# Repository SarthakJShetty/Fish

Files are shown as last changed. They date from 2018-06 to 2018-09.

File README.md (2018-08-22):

# Open Source Robotic Fish

This repository is dedicated to the development of the predatory robotic fish, developed at the [Theoretical Ecology and Evolution Laboratory](https://teelabiisc.wordpress.com/ "TEE-Lab, IISc"), [Indian Institute of Science](https://www.iisc.ac.in "Indian Institute of Science, Bengaluru").

### :warning: Code is buggy :warning:

### Introduction:
The robotic fish developed was used to study the aggregation and swarming characteristics of the <em><a title="Serpae tetra" href="https://en.wikipedia.org/wiki/Serpae_tetra" target="_blank">Serpae tetra</a></em> species of fish.

### Construction:
 - The body of the Fish is made of extruded polystyrene (thermocol). The [design](https://github.com/SarthakJShetty/Fish/tree/master/Design_Files/Mechanical_Design/Structure_Design "Mechanical Designs") was made in SolidWorks, and carved using a crafting blade.

 - The Fish is maneuvered using a joystick controller through the [pygame](Pygame.org "pygame") library for Python. A list of supported controllers is given [here](https://www.pygame.org/docs/ref/joystick.html "pygame"). We have tried out a number of joysticks, such as the [XBox 360 controller](https://www.amazon.com/Xbox-360-Wireless-Controller-Packaging-Black/dp/B073WJCQGT/ref=sr_1_4?ie=UTF8&qid=1530160595&sr=8-4&keywords=xbox+360+controller "XBox 360 controller"), and the [Logitech Extreme 3D Pro Gamepad](https://www.amazon.com/Extreme-3D-Pro-Joystick-Windows/dp/B00009OY9U/ref=sr_1_1?s=videogames&ie=UTF8&qid=1530160648&sr=1-1&keywords=logitech+extreme+pro "Logitech Extreme 3D Pro").

 - The Fish is controlled through an Arduino UNO, which communicates with the computer running ```pygame``` through a [Bluetooth module](https://www.amazon.com/HiLetgo%C2%AE-Wireless-Bluetooth-Transceiver-Arduino/dp/B071YJG8DR/ref=sr_1_1_sspa?ie=UTF8&qid=1530698951&sr=8-1-spons&keywords=hc05&psc=1 "HC-05 Bluetooth Module"), mounted on it's head.

 - A [SHARP Distance Sensor GP2Y0A21YK0F](https://www.pololu.com/category/79/sharp-distance-sensors "Sharp Distance Sensor GP2Y0A21YK0F") was used to judge the distance between the fish and obstacles up ahead.

 - The Fish was encased in a layer of polythene to ensure waterproofing while operating underwater. Specifically, the joints between successive links was encased in a skin-like layer of polythene.

 - The necessary propelling movements were provided by a series of 3 [Tower SG90 Servo Motors](https://servodatabase.com/servo/towerpro/sg90 "Tower S690 Servo Motors").

 - A pair of [9V batteries](https://www.amazon.com/AmazonBasics-Everyday-Alkaline-Batteries-8-Pack/dp/B00MH4QM1S "9V Batteries") were used in series to provide the necessary electric power for the operation of the fish.

### Fritzing Diagram:
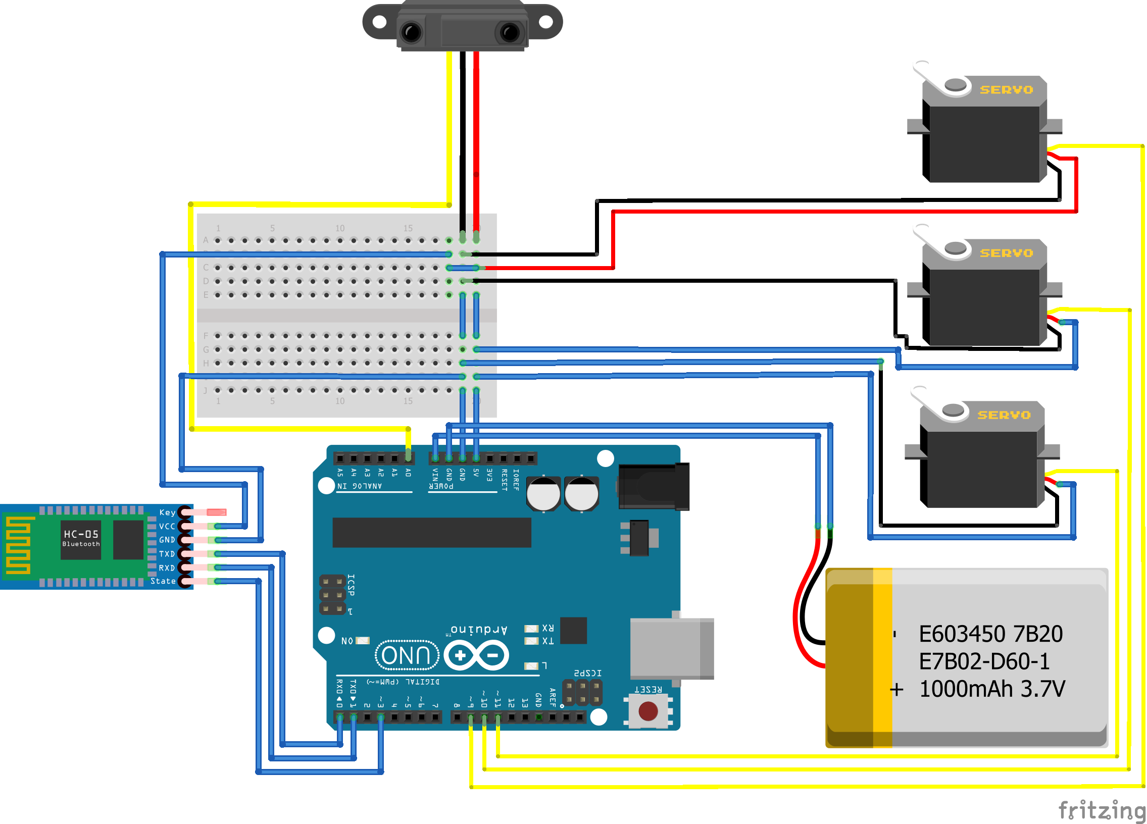
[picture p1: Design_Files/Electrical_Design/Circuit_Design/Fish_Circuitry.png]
Fritzing Diagram

<figcaption align="center"><strong>Fig 1.</strong><em> Fritzing diagram of electrical wiring.</em>
<em><strong>Note:</strong> 3.7V LiPo is for representation purposes only.</em></figcaption>

### SolidWorks Model:
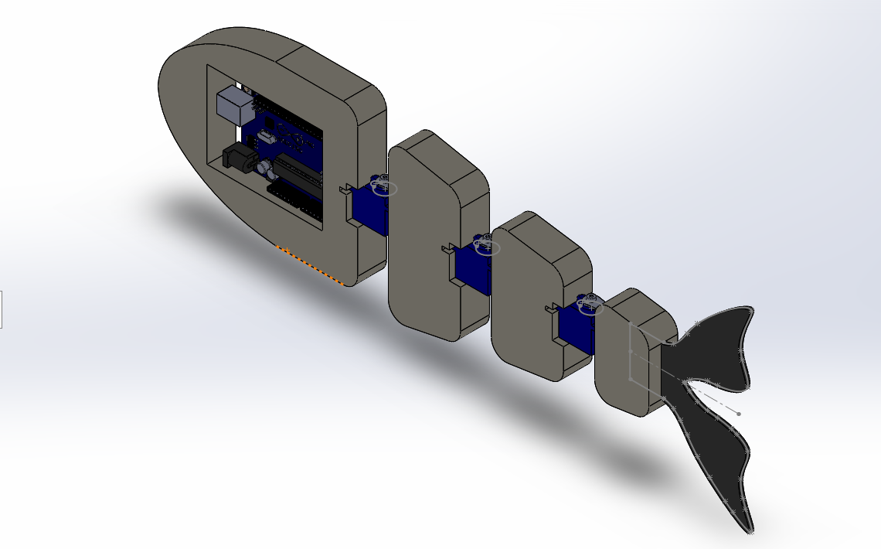
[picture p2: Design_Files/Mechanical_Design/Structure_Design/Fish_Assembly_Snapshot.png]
SolidWorks Model

<figcaption align="center"><strong>Fig 2.</strong><em> SolidWorks assembly of mechanical structure.</em></figcaption>

### Command Flowchart:
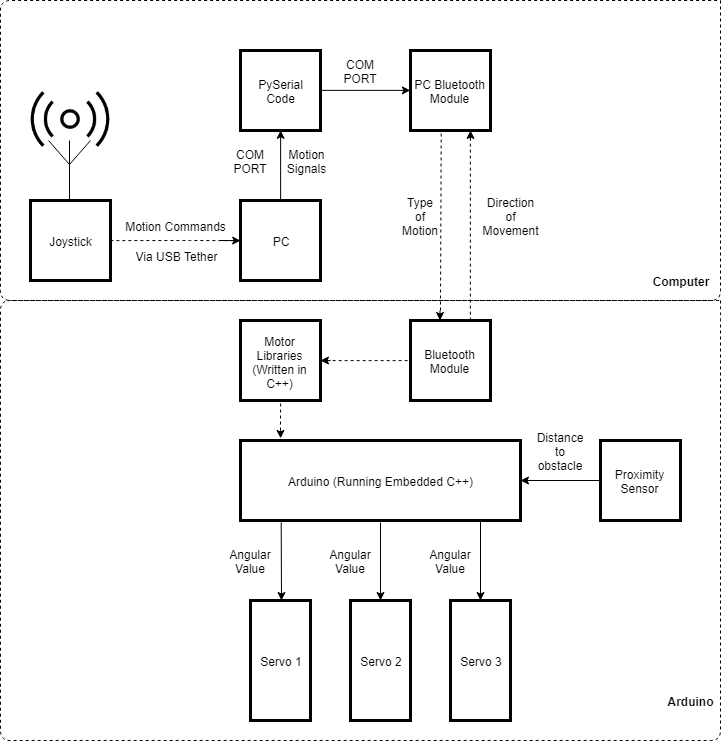
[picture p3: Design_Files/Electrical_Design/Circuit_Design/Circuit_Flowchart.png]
Command flowchart

<figcaption align="center"><strong>Fig 3.</strong><em> Flowchart of commands.</em></figcaption>

### Working:
 1. The electrical connections are made as shown in the <a title="Fritzing Diagram" href="https://github.com/SarthakJShetty/Fish/master/Design_Files/Electrical_Design/Circuit_Design/Fish_Circuitry.png" alt="Fritzing Diagram">Fritzing diagram</a>.

 2. Once the connections are made and checked (to prevent short circuiting underwater!), the batteries are connected to the battery headers provided in the circuit.

 3. The SHARP sensors are obstructed to check if the necessary commands are executed (in this case the ```C_MOVE()``` function would be executed).

 4. Once the [Joystick.py](https://github.com/SarthakJShetty/fish/tree/master/Code/Joystick_Code/Joystick_Code.py) has been executed, wait for 5 seconds as the [EEPROM_Code.cpp](https://github.com/SarthakJShetty/Fish/tree/master/Code/CPP_Code/EEPROM_Flush_Code.cpp) script executes and flushes the EEPROM on-board the UNO to prevent interferences from previous stored values.

 5. The Fish can be maneuvered as required using the left analog stick of the joystick. Three movements are possible:
	- [Forward](https://github.com/SarthakJShetty/Fish/tree/master/Code/CPP_Code/Stable_Movement_Code.cpp)- The Fish moves in an S-type movement.
	- [Left](https://github.com/SarthakJShetty/Fish/tree/master/Code/CPP_Code/Stable_Movement_Code.cpp)- The Fish moves in a C-type movement, deflecting towards the left.
	- [Right](https://github.com/SarthakJShetty/Fish/tree/master/Code/CPP_Code/Stable_Movement_Code.cpp)- The Fish moves in a C-type movement, deflecting towards the right.
	- [Obstacle Avoidance](https://github.com/SarthakJShetty/Fish/tree/master/Code/CPP_Code/Stable_Movement_Code.cpp)- The Fish moves in a C-type movement, deflecting towards the left. 

 6. The Fish operates either through the controls of the user, through the joystick, or it continuously moves in an S-type fashion, until it encounters an obstacle, thereafter which it executes a C-type movement.

### Build-log:
You can check out the <a title="Build-log" href="https://github.com/SarthakJShetty/Fish/tree/master/build-log.md">build-log</a> for a detailed progress report.

### Known Issues:

 1. Occasionally, the Bluetooth module on-board losses communication link with the Bluetooth on the PC. When this happens, close the pygame dialog and rerun the Joystick_Code.py script to establish control once again (<strong>this issue has now been resolved by connecting the Bluetooth module to a 3.3V voltage supply.</strong>)

 2. The Arduino will reboot, if sufficient power is not provided. Thus, we suggest the use of LiPo batteries to provide a more reliable and lasting power source. We are currently using <a title="12V LiPo battery" href="" target="_blank">12V, 2000mAh LiPo batteries</a> (testing this right now).

 3. Communication link between the UNO and the computer will not be active until the `EEPROM_Flush_Code.cpp` has been executed (approx 5 seconds), thereafter which the LED on the UNO associated with GPIO pin 13 will glow a bright orange (depending on the make of the Arduino board).

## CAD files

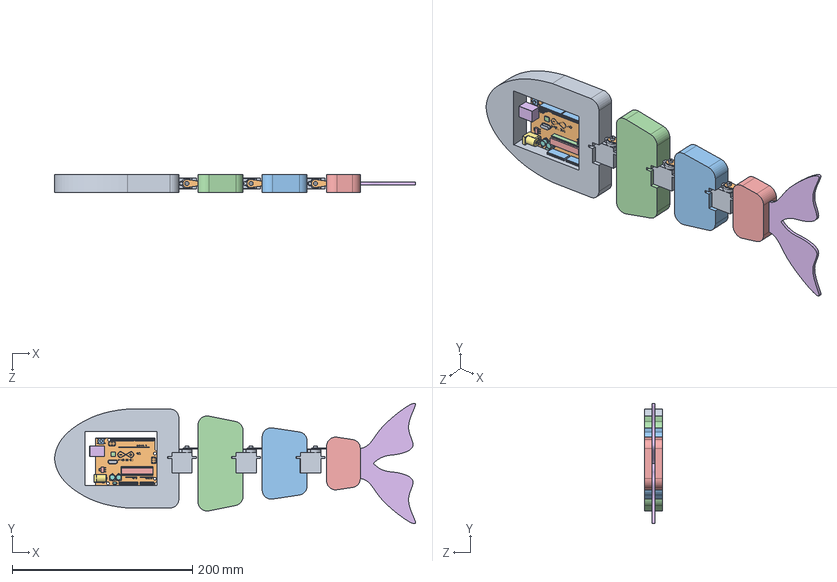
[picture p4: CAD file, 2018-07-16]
Design_Files/Mechanical_Design/Structure_Design/Fish_Assembly.SLDASM
401.1 x 133.8 x 20.0 mm
PCB UNO
Buton
base chip
foot (chip) x 4
foot (big chip) x 24
Condensateur x 2
Crystal
ICSP x 2
Pins Connection Shield
Small Chip
Transistor
USB
Alimentation
Resistance
Servo Motor (SG90) x 3
Servo_Horn x 3
Tail_Fin

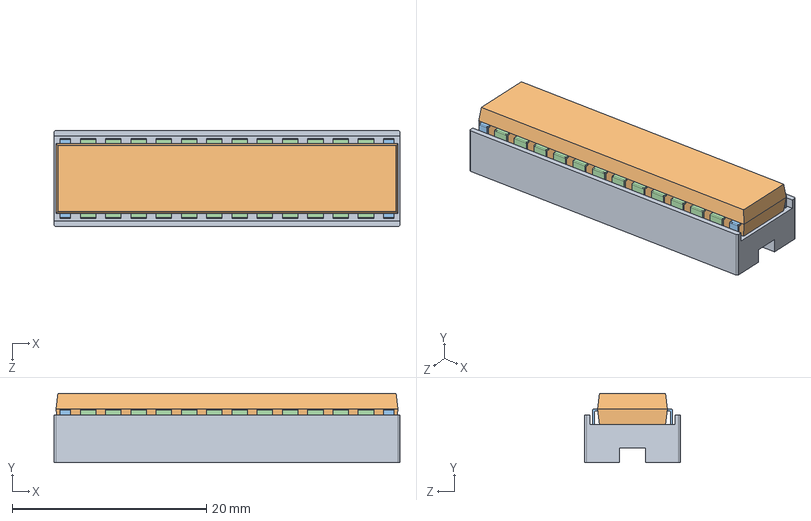
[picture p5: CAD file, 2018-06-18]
Design_Files/Electrical_Design/Arduino_Design/Chip.SLDASM
35.6 x 7.10 x 9.90 mm
base chip
foot (chip) x 4
foot (big chip) x 24

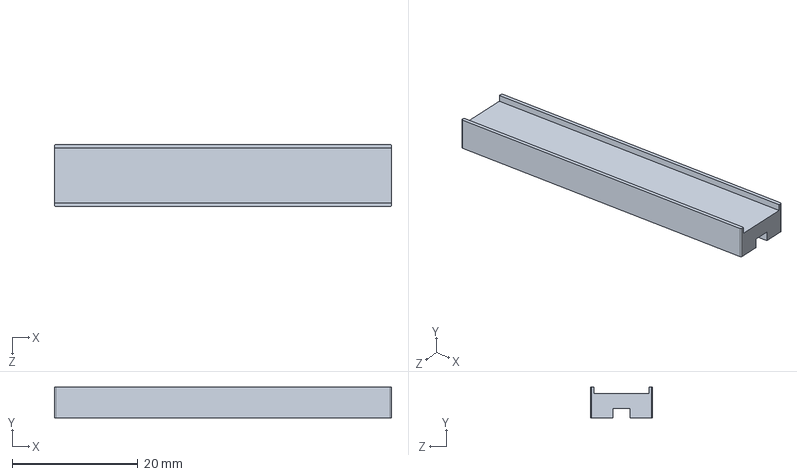
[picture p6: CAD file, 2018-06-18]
Design_Files/Electrical_Design/Arduino_Design/base chip.SLDPRT
53.6 x 4.90 x 9.90 mm

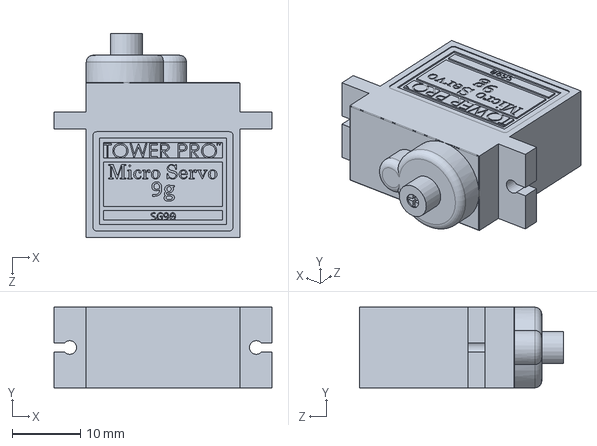
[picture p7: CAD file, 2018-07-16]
Design_Files/Mechanical_Design/Servo_Design/Servo Motor (SG90).SLDPRT
31.9 x 11.8 x 29.9 mm

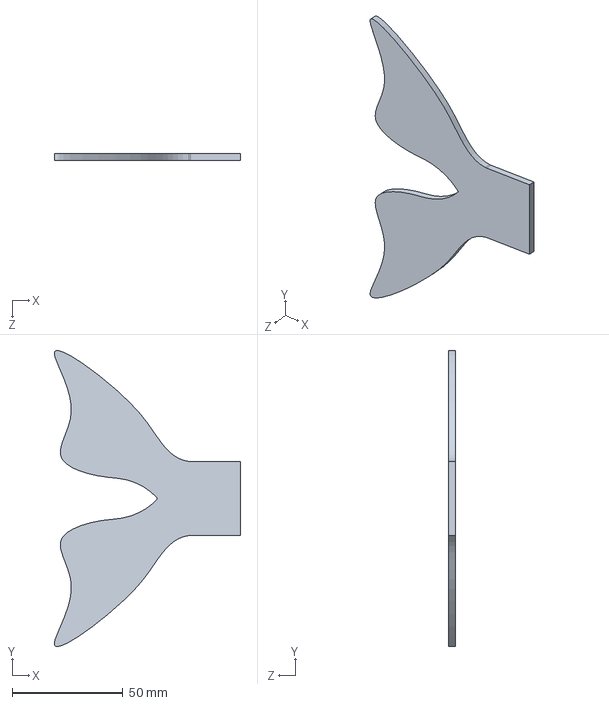
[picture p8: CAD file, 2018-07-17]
Design_Files/Mechanical_Design/Structure_Design/Tail_Fin.SLDPRT
84.3 x 133.8 x 3.00 mm

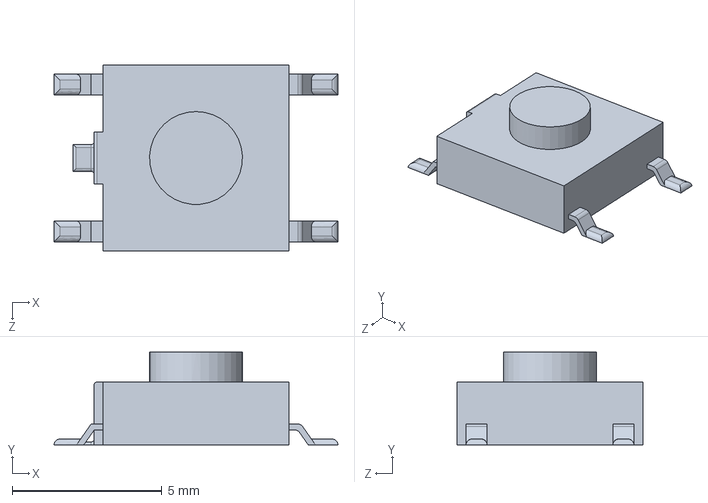
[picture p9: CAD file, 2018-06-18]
Design_Files/Electrical_Design/Arduino_Design/Buton.SLDPRT
9.48 x 3.10 x 6.20 mm

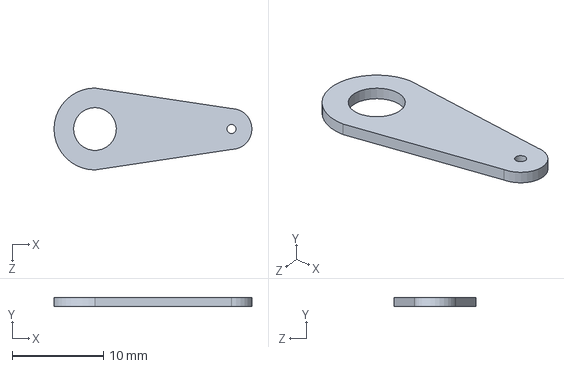
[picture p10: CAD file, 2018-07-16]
Design_Files/Mechanical_Design/Servo_Design/Servo_Horn.SLDPRT
21.8 x 1.00 x 9.00 mm

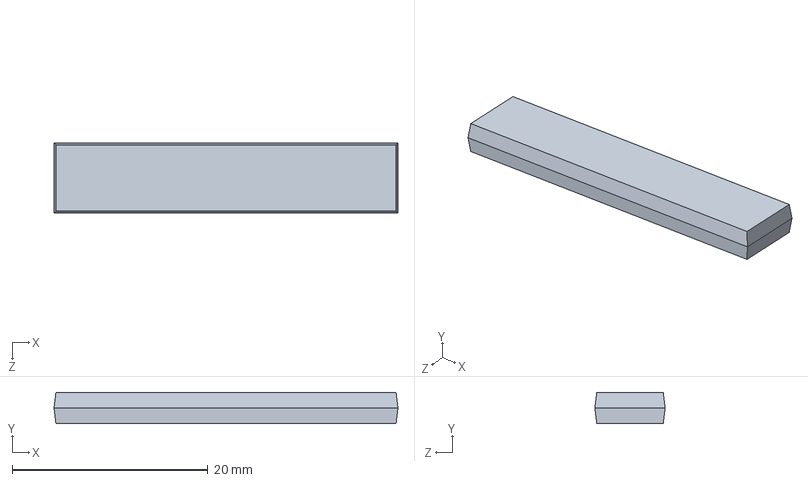
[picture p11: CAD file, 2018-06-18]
Design_Files/Electrical_Design/Arduino_Design/box.SLDPRT
35.2 x 3.20 x 7.19 mm

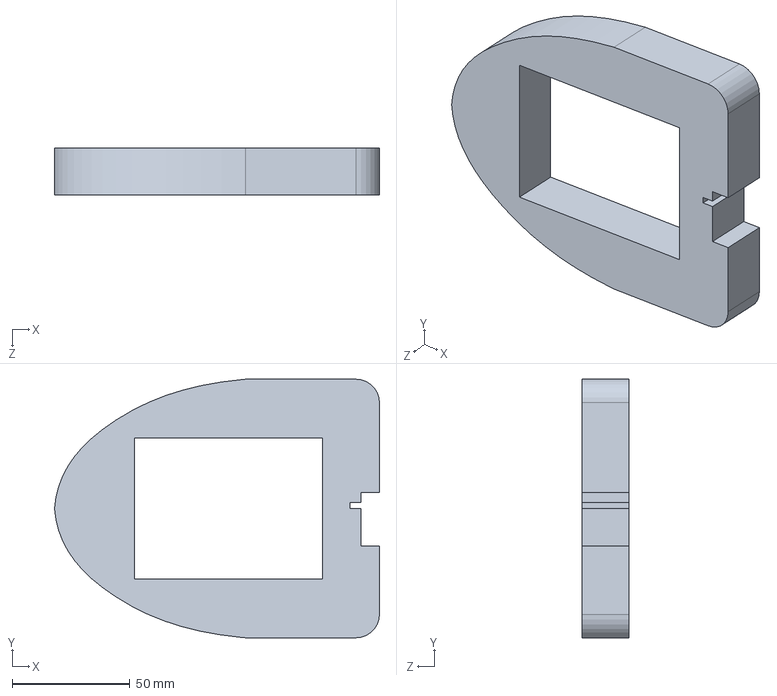
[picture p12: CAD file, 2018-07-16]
Design_Files/Mechanical_Design/Structure_Design/Body.SLDPRT
138.2 x 110.0 x 20.0 mm

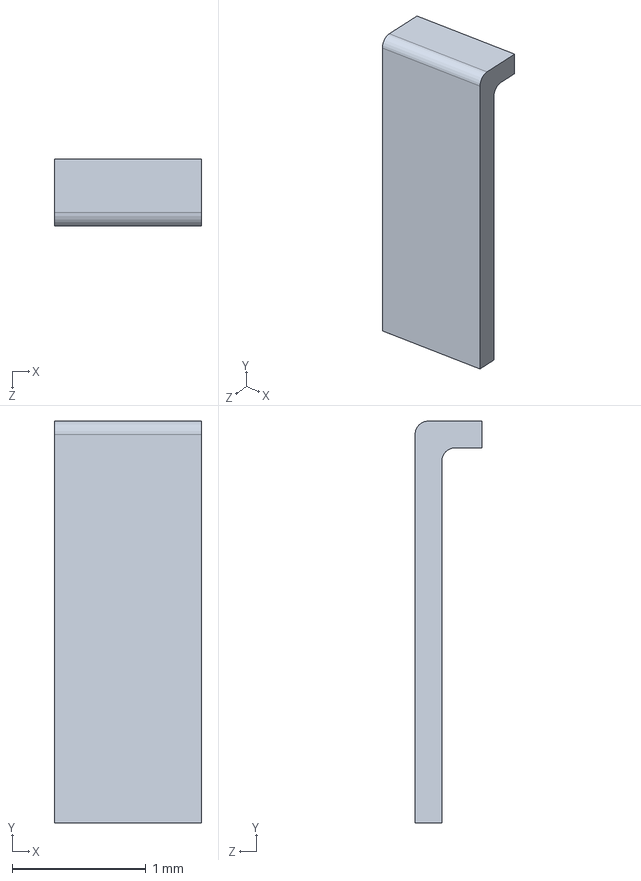
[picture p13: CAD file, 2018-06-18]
Design_Files/Electrical_Design/Arduino_Design/foot (chip).SLDPRT
1.10 x 3.00 x 0.5 mm

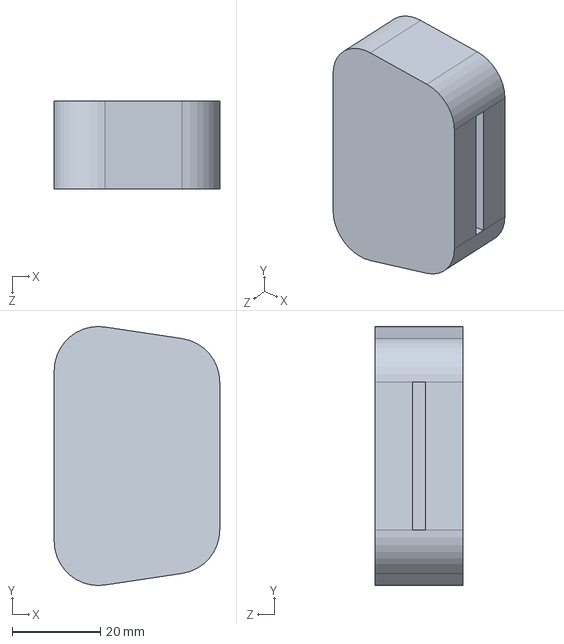
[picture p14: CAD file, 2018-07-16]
Design_Files/Mechanical_Design/Structure_Design/Body_4.SLDPRT
37.5 x 58.6 x 20.0 mm

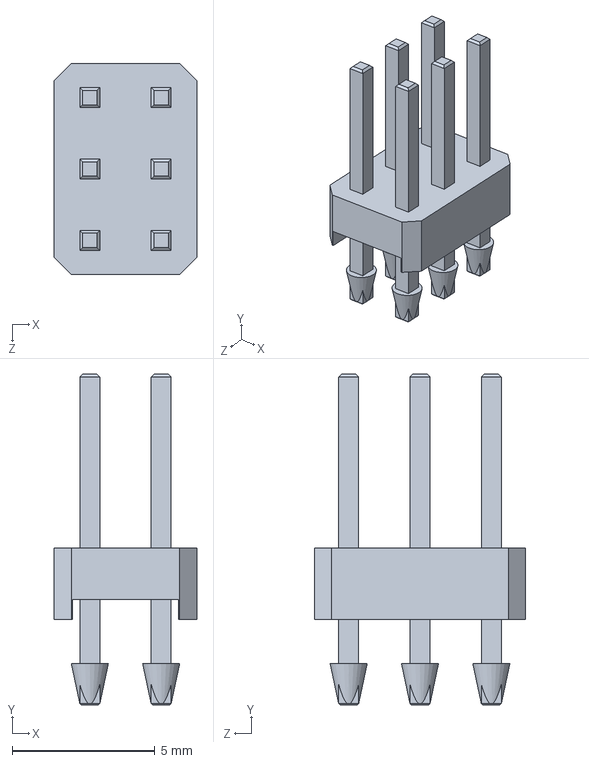
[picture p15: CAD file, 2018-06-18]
Design_Files/Electrical_Design/Arduino_Design/ICSP.SLDPRT
5.00 x 11.6 x 7.40 mm

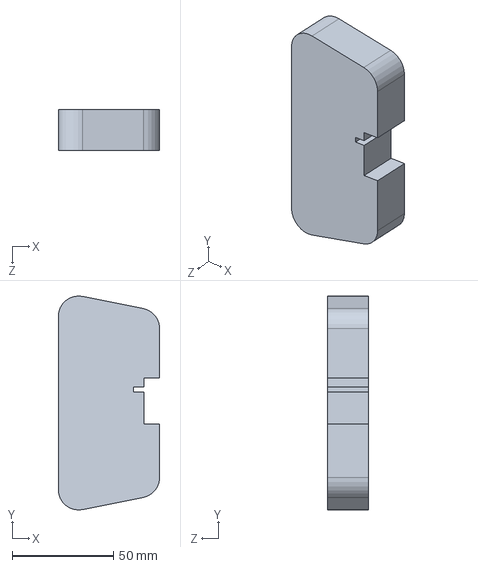
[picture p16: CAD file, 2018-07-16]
Design_Files/Mechanical_Design/Structure_Design/Body_2.SLDPRT
50.0 x 105.6 x 20.0 mm

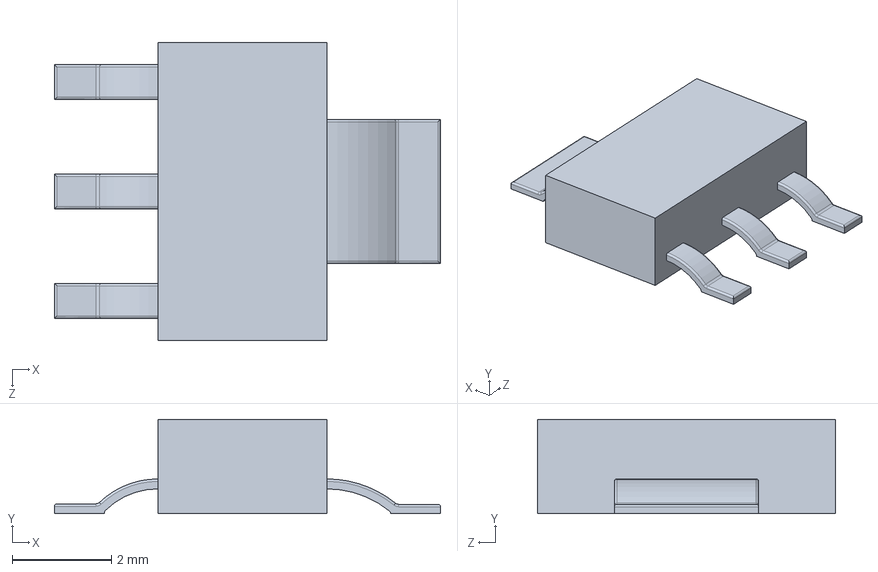
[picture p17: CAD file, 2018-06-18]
Design_Files/Electrical_Design/Arduino_Design/Transistor.SLDPRT
7.76 x 1.90 x 6.00 mm

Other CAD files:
Design_Files/Mechanical_Design/Structure_Design/Body_3.SLDPRT
Design_Files/Electrical_Design/Arduino_Design/foot (big chip).SLDPRT
Design_Files/Electrical_Design/Arduino_Design/Alimentation.SLDPRT
Design_Files/Electrical_Design/Arduino_Design/Condensateur.SLDPRT
Design_Files/Electrical_Design/Arduino_Design/Crystal.SLDPRT
Design_Files/Electrical_Design/Arduino_Design/PCB UNO.SLDPRT
Design_Files/Electrical_Design/Arduino_Design/Pins Connection Shield.SLDPRT
Design_Files/Electrical_Design/Arduino_Design/Resistance.SLDPRT
Design_Files/Electrical_Design/Arduino_Design/USB.SLDPRT
Design_Files/Mechanical_Design/Structure_Design/Fish_Assembly.SLDDRW

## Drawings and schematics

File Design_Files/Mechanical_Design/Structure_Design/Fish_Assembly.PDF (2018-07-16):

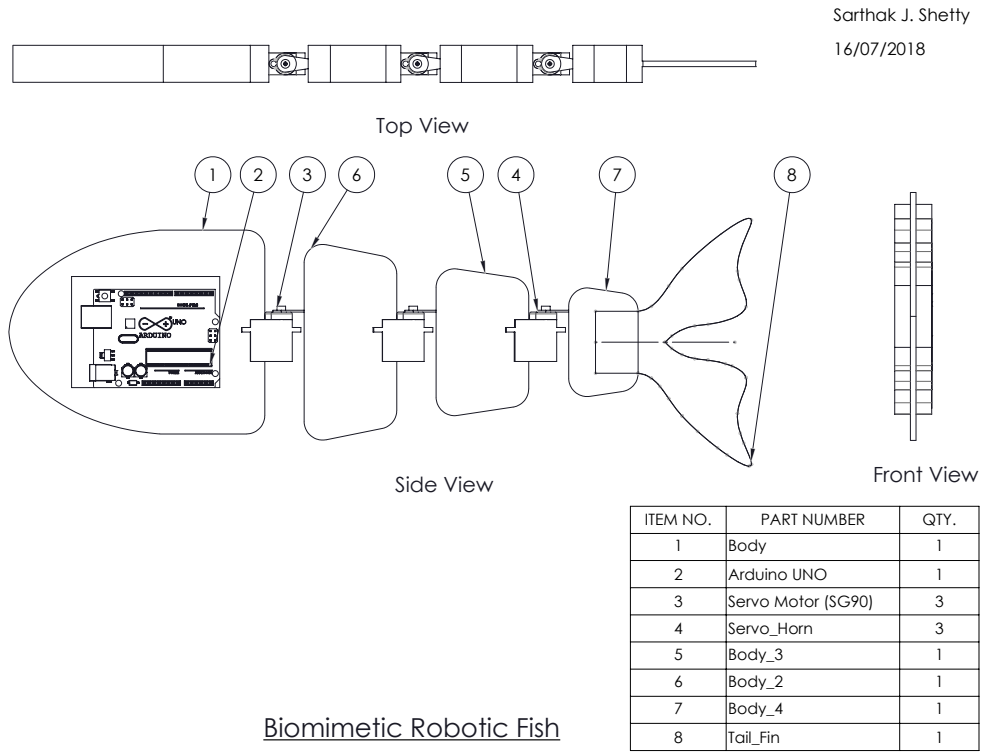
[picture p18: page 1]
Sarthak J. Shetty; Side View; Top View; Front View

ITEM NO. | PART NUMBER | QTY.
1 | Body | 1
2 | Arduino UNO | 1
3 | Servo Motor (SG90) | 3
4 | Servo_Horn | 3
5 | Body_3 | 1
6 | Body_2 | 1
7 | Body_4 | 1
8 | Tail_Fin | 1

Biomimetic Robotic Fish

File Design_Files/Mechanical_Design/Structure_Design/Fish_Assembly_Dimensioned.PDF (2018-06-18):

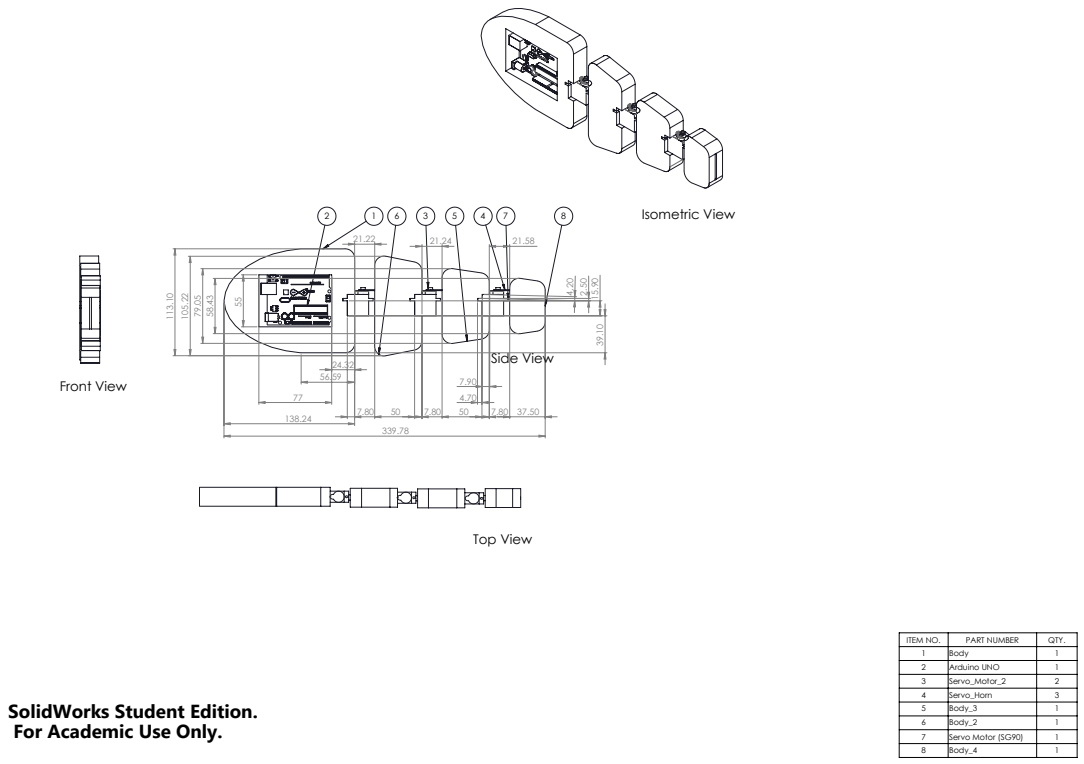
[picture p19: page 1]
Side View; Isometric View; Front View; Top View

ITEM NO. | PART NUMBER | QTY.
1 | Body | 1
2 | Arduino UNO | 1
3 | Servo_Motor_2 | 2
4 | Servo_Horn | 3
5 | Body_3 | 1
6 | Body_2 | 1
7 | Servo Motor (SG90) | 1
8 | Body_4 | 1

SolidWorks Student Edition.
For Academic Use Only.

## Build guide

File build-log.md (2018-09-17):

### Progress Log:

- <strong>Date:</strong> 28/05/2018
	- Just wrote code.
	- Yet to implement on Arduino.
 	- Will be doing that tomorrow.
 	- Need to add a <a title="README.md" target="_blank" href="https://github.com/SarthakJShetty/Fish/blob/master/README.md">README</a>.

- <strong>Date:</strong> 29/05/2018
 	- Code now works with sensor.
 	- Added a piece of code to convert volts to distance.

- <strong>Date:</strong> 60/05/2018
 	- Updated Bluetooth Code.
 	- Bluetooth now works over COM4 port.
 	- ```println()``` statements look much cleaner now

- <strong>Date:</strong> 31/05/2018
 	- Added EEPROM flush. Not much of an improvement.
 	- Bluetooth has not been integrated here.
	- Bluetooth code has been introduced, albeit very buggy as of now.

- <strong>Date:</strong> 08/05/2018
 	- Joystick can be used to control the fish now. Attempting on a wired controller though.
 	- Interference. Need to upload a SLAVE communication.

- <strong>Date:</strong> 09/06/2018
 	- DualShock3 replaced with XBox 360 Wireless knockoff controller.
 	- Works much better now.
 	- SLAVE protocol has been established. Works much better.

- <strong>Date:</strong> 10/06/2018
 	- BLuetooth module has been converted into a one-way system, i.e. slave communication
 	- RX/TX can be connected simultaneously, no obstruction to communication from controller.

- <strong>Date:</strong> 13/06/2018
 	- Code has been successfully tested on fish.
 	- This code has been converted into a ```.cpp``` library, to make the Arduino code cleaner.

- <strong>Date:</strong> 15/06/2018
 	- The thermocol has ripped. Adhesive applied and trying to fix it.
 	- Code seems to be working well. Angles seem to be too big though.

- <strong>Date:</strong> 03/07/2018
	- Embargo due to mechanical issues.
	- A polythene wrapper has been used as a final layer for waterproofing the structure.
	- The issue is with fit. Almost fixed it.
	- Should have a great Fish by this weekend. Fingers crossed.
	- Try to code a more harmonic motion of Fish body.

- <strong>Date:</strong> 09/07/2018
	- Movement seems to work well, even without harmonic motion integration.
	- <strong>Important:</strong>```ICSP``` pins should not be used for power supply. ```V(in)``` pin solely supports 5V. ```V(in)``` should be used, along with corresponding ```GND``` pin.
	- Looking forward to 3D printing some of the components.

- <strong>Date:</strong> 14/07/2018
	- Plastic has been bound.
	- Compensations have been provided.
	- Waiting for adhesive to dry up.

- <strong>Date:</strong> 15/07/2018
	- Rubber based adhesive used to fill the last remaining holes.
	- Adhesive also used to coat the battery. Multiple times.
	- Tail fin and fish design <a title="Tail fin" href="https://raw.githubusercontent.com/SarthakJShetty/Fish/master/Design%20Files/Mechanical_Design/Fish_Design/Fish_Assembly.png" target="_blank">updated</a>. Looks less like a kayaking paddle now.

- <strong>Date:</strong> 16/07/2018
	- Fish works great with plastic binding now.
	- Movements are unforced. Feels smooth. Finally this works.
	- Filled the last remaining slots and gaps in the plastic. Will cut out a cover for the Sharp sensor.
	- 3D printing of fin underway. We're almost there.

- <strong>Date:</strong> 17/07/2018
	- Solved the great repository debacle.
	- Almost done. 3D printing yet to be completed.

- <strong>Date:</strong> 13/08/2018
	- Waterproofing works (almost; 90%ish).
	- Fin has been 3D printed. Works great.
	- Had a buoyancy debacle. Almost sorted.
	- If waterproofing is fixed, then we can begin the actual testing.

- <strong>Date:</strong> 22/08/2018
	- Iterated through at least 8 skins designs for waterproofing.
	- Currently testing the 9th one. This should work.
	- To vary buoyancy, cast iron blocks of different weights can be used.
	- Currently using a 660 grams one that provides a above surface height of about 8mm.
	- Just about right for the antennae to pop up from the surface.

<strong>Date:</strong> 17/09/2018
	- Skin is mostly impenetrable and sealed.
	- An average height of 3 cm penetrates the skin.
	- Weight has been optimized to 498gm. Buoyancy is just right.
	- Will test with air-tight enclosure for switch next. Should be ready by Thursday.

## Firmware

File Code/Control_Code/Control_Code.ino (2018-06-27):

/* Flow:
 * Autonomous Mode - without controller (not implemented in this phase).
 * Borrow functions from Stable_Code for S/C Movement for Bluetooth Controlled Motion.
 * Borrow fucntions from Stable_Code for S/C Movement for Autonomous Motion

[LOG] Date: 31/05/2018
[LOG] -EEPROM Code has been implemented.
[LOG] -Movement Code has been implemented.
[LOG] -Bluetooth Code has been implemented.
[LOG] -Sensor Code has been implemented.
[LOG] -Detection has been achieved.
[LOG] -Conditional Movement has been acheived.


[INFO] -Here, the number of joints is assumed as 3.
[INFO] -Wait for 5 seconds (approximate) before sending commands through controller. 
[INFO] -EEPROM Flush has to take place before operation.
[INFO] -COM4 is used as default communication port for bluetooth.
[INFO] -COM3 is used as default communicaation port for Serial Communication.
*/

#include<Servo.h>
#include<F:\Google Drive\IISc Files\Code\CPP_Code\EEPROM_Flush_Code.cpp>
//#include<F:\Google Drive\IISc Files\Code\CPP_Code\Unstable_Movement_Code.cpp>
#include<F:\Google Drive\IISc Files\Code\CPP_Code\Stable_Movement_Code.cpp>
#include<F:\Google Drive\IISc Files\Code\CPP_Code\Sensor_Code.cpp>
void setup() {
  Serial.begin(9600);
  motor_1.attach(9);
  motor_2.attach(10);
  motor_3.attach(11);
  EEPROM_FLUSH();
}

void loop() {
    int SENSOR_VAR=SENSOR_READ();
    if(SENSOR_VAR>=5){
    if(Serial.available()){
    int BLUETOOTH_VAR;
    BLUETOOTH_VAR=Serial.read();
    if(BLUETOOTH_VAR=='1'){
    S_MOVE();}
    else if(BLUETOOTH_VAR=='2'){
    C_MOVE_RIGHT();}
    else if(BLUETOOTH_VAR=='3'){
    C_MOVE_LEFT();}
    }
    }
  else if(SENSOR_VAR<5){
    C_MOVE();}
}

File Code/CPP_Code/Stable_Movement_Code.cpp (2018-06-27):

/*
[INFO] -The code is organised into respective folders.
[INFO] -Other than CPP headers. They are kept seperately.

[LOG] Date: 28/05/2018
[LOG] -Just wrote code.
[LOG] -Yet to implement on Arduino.
[LOG] -Will be doing that tomorrow.
[LOG] -Need to add a README.

[LOG] Date: 29/05/2018
[LOG] -Code now works with sensor.
[LOG] -Added a piece of code to convert volts to distance.

[LOG] Date: 60/05/2018
[LOG] -Updated Bluetooth Code.
[LOG] -Bluetooth now works over COM4 port.
[LOG] -println statements look much cleaner now

[LOG] Date: 31/05/2018
[LOG] -Added EEPROM flush. Not much of an improvement.
[LOG] -Bluetooth has not been integrated here.
[LOG] -Bluetooth code has been introduced, albeit very buggy as of now.

[LOG] Date: 08/05/2018
[LOG] -Joystick can be used to control the fish now. Attempting on a wired controller though.
[LOG] -Intereference. Need to upload a SLAVE communication.

[LOG] Date: 09/06/2018
[LOG] -DualShock3 replaced with Xbox 360 Wireless knockoff controller.
[LOG] -Works much better now.
[LOG] -SLAVE protocol has been established. Works much better.

[LOG] Date: 10/06/2018
[LOG] -BLuetooth module has been converted into a one-way system, i.e. slave communication
[LOG] -RX/TX can be connected simultaneously, no obstruction to communication from controller.

[LOG] Date: 13/06/2018
[LOG] -Code has been successfully tested on fish.
[LOG] -This code has been converted into a .cpp libray, to make the Arduino code cleaner.

[LOG] Date: 15/06/2018
[LOG] -The thermocol has ripped. Adhesive applied and trying to fix it.
[LOG] -Code seems to be working well. Angles seem to be too big though.
------------------------------------------------------------------------------------------

CODE BELOW THIS, UPTO THE END OF COMMENTS IS ARDUINO CODE BEFORE CONVERSION TO CPP LIBRARY.

------------------------------------------------------------------------------------------
*/

//Code to be run on the Robotic Fish
//Assume n=3 (number of joints), j=n+1=4(number of links).
//Two types of motions are possible here, C and S movement.
//Movements are classified based on top view of the fish.
//Refer README for more Documentation.
//Servo motors are being defined here from Servo.h instance
/*Servo motor_1,motor_2,motor_3;
#define sensor A0

//Functions, S and C are being defined here.
void func_s();
void func_c();

//Motors are attached to the pins here. 9,10,11 are analog pins.

void setup(){

pinMode(13,OUTPUT);
j=EEPROM_FLUSH();
analogReference(DEFAULT);
Serial.begin(9600);
motor_1.attach(9);
motor_2.attach(10);
motor_3.attach(11);

//Sharp Infrared Sensors are used for INPUT.

}

void loop(){
  BLUE_COM();
float volts = analogRead(sensor)*0.0048828125;  // value from sensor * (5/1024)
  int reading = 13*pow(volts, -1);
  //delay(1000);
  //Value from the sensor(s) is read here.
  if(j>0)Serial.println("EEPROM has been flushed");
Serial.print("Distance: "); Serial.println(reading);
  //This condition checks if obstacle has been detected. In this case, no obstacle.
  if(reading>=10){

    //Function S has been triggered here.
    func_s();
  }

  //Obstacle has been detected by the sensor in this case.
  else if(reading<10){

    //Function C has been triggered in this case.
    func_c();
  }
}
---------------------------------------------------------------------------------------------

END OF REPLACED ARDUINO CODE.

---------------------------------------------------------------------------------------------

//This is executed when the obstacle has been detected on the left.
//Each joint has been given an angle of 60 degrees. As we move away from n=1. each angle gets multiplied by 2
//90 degrees is used as the median position, i.e. starting position.
//For S and C movements median is taken as 90 degrees.

/*Four types of movements are employed in this case:
1. S_MOVE()-Used for forward movement (Top view of the fish looks like an S)
2. C_MOVE()-Used for right movement, away from the obstacle
3. C_MOVE_RIGHT()-Same as C_MOVE()
4. C_MOVE_LEFT()-Used for left movement, away from the obstacle

----------------------------------------------------------------------------------------------*/

#include<Servo.h>
Servo motor_1,motor_2,motor_3;
void S_MOVE(){
  int angleIncrementer=90;
for(angleIncrementer=90;angleIncrementer<=120;angleIncrementer++){
  motor_1.write(angleIncrementer);
  motor_2.write(angleIncrementer);
  motor_3.write(angleIncrementer);
  delay(10);
  }

for(angleIncrementer=120;angleIncrementer>=60;angleIncrementer--){
  motor_1.write(angleIncrementer);
  motor_2.write(angleIncrementer);
  motor_3.write(angleIncrementer);
  delay(10);
}

for(angleIncrementer=60;angleIncrementer<=90;angleIncrementer++){
  motor_1.write(angleIncrementer);
  motor_2.write(angleIncrementer);
  motor_3.write(angleIncrementer);
  delay(10);
}
}

void C_MOVE(){

  //Serial.println("You have entered the C - Right Function");

  int angleIncrementer=90;
  for(angleIncrementer=90;angleIncrementer<=120;angleIncrementer++){
    motor_1.write(angleIncrementer+5);
    motor_2.write(angleIncrementer);
    motor_3.write(angleIncrementer);
    delay(10);
  }
  
  for(angleIncrementer=120;angleIncrementer>=90;angleIncrementer--){
    motor_1.write(angleIncrementer-5);
    motor_2.write(angleIncrementer);
    motor_3.write(angleIncrementer);
    delay(10);
  }
  }

void C_MOVE_RIGHT(){

  //Serial.println("You have entered the C - Right Function");
  
  int angleIncrementer=90;
  for(angleIncrementer=90;angleIncrementer<=120;angleIncrementer++){
    motor_1.write(angleIncrementer+5);
    motor_2.write(angleIncrementer);
    motor_3.write(angleIncrementer);
    delay(10);
  }
  
  for(angleIncrementer=120;angleIncrementer>=90;angleIncrementer--){
    motor_1.write(angleIncrementer-5);
    motor_2.write(angleIncrementer);
    motor_3.write(angleIncrementer);
    delay(10);
  }
  }

void C_MOVE_LEFT(){
  
  //Serial.println("You have entered the C - Left Function");
  
  int angleIncrementer=90;
  for(angleIncrementer=90;angleIncrementer>=60;angleIncrementer--){
    motor_1.write(angleIncrementer+5);
    motor_2.write(angleIncrementer);
    motor_3.write(angleIncrementer);
    delay(10);
  }

  for(angleIncrementer=60;angleIncrementer<=90;angleIncrementer++){
    motor_1.write(angleIncrementer-5);
    motor_2.write(angleIncrementer);
    motor_3.write(angleIncrementer);
    delay(10);
  }
}

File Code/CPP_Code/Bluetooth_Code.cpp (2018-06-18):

//This code is uded to communicate over bletooth with the Arduino.
//loop and setup are commented out because the code is seen as C++ code by the Arduino compiler.
//For detailed [LOG] and [INFO] have a look at the Stable_Movement.cpp code.

//----------------------------------------------------------------------------------------------


#include<Servo.h>
//#include<F:\Google Drive\IISc Files\Code\EEPROM_Flush_Code\EEPROM_Flush_Code.cpp>
void BLUE_COM(){
Servo motor1, motor2, motor3;
//void setup(){
  motor1.attach(9);
  motor2.attach(10);
  motor3.attach(11);
  Serial.begin(9600);
  pinMode(13,OUTPUT);
  //j=EEPROM_FLUSH();
//}
//void loop(){
  int i;
if(Serial.available()){
  //if(j>0)Serial.println("[INFO] EEPROM has been flushed");
  //Serial.println("[INFO] Connection established");}
  char VAL;
  VAL=Serial.read();
  if(VAL=='1'){
        //Serial.println("[STATUS] LED is ON");
        digitalWrite(13,HIGH);
 for(i=0;i<=90;i++){

    motor1.write(i);
    motor2.write(i);
    motor3.write(i);
    delay(10);
    }
    }
  else if(VAL=='0'){
        digitalWrite(13,LOW);
        //Serial.println("[STATUS] LED is OFF");
   for(i=90;i>=0;i--){
    motor1.write(i);
    motor2.write(i);
    motor3.write(i);
    delay(10);
    }
    }}
  //}

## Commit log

2018-06-18 Adding designs
    [Alimentation.SLDPRT, Arduino UNO.SLDASM, Body.SLDPRT, Body_2.SLDPRT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]
2018-06-18 Removing older design
    [Alimentation.SLDPRT, Arduino UNO.SLDASM, Body.SLDPRT, Body_2.SLDPRT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]
2018-06-18 Accidentally added these files
    [Body.SLDPRT, Fin.SLDPRT, Fin_Left.SLDPRT, Fish_Assembly.SLDASM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]
2018-06-18 Renaming files
    [Alimentation.SLDPRT, Arduino UNO.SLDASM, Body.SLDPRT, Body_2.SLDPRT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]
2018-06-18 Old files removed
    [Alimentation.SLDPRT, Arduino UNO.SLDASM, Body.SLDPRT, Body_2.SLDPRT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]
2018-06-18 Renamed file
    [Alimentation.SLDPRT, Arduino UNO.SLDASM, Buton.SLDPRT, Chip.SLDASM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]
2018-06-18 Will move files to /Images
    [Fish_Circuitry.fzz]
2018-06-18 Adding Circuit and Design images
    [Fish_Circuitry.fzz]
2018-06-18 Removing folders, replacing with files
    [Fish_Circuitry.fzz]
2018-06-18 Adding pictures, SLDDRW and sesign
    [Fish_Assembly.SLDDRW]
2018-06-27 Updating Fritzing circuit
    [Fish_Circuitry.fzz]
2018-06-27 Updated wiring in README
2018-06-27 Removed Images directory
    [Fish_Assembly.SLDDRW]
2018-06-27 Gathering electrical files together
    [Alimentation.SLDPRT, Arduino UNO.SLDASM, Buton.SLDPRT, Chip.SLDASM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]
2018-06-27 Gathered mechanical design files together
    [Alimentation.SLDPRT, Arduino UNO.SLDASM, Body.SLDPRT, Body_2.SLDPRT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]
2018-06-27 Relocated these files
    [Alimentation.SLDPRT, Arduino UNO.SLDASM, Buton.SLDPRT, Chip.SLDASM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]
2018-06-27 Relocated Files
    [Alimentation.SLDPRT, Arduino UNO.SLDASM, Body.SLDPRT, Body_2.SLDPRT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]
2018-06-27 Moved files to electrical design
    [Servo Motor (SG90).SLDPRT]
2018-06-27 Updated bulleting in the Known Issues section
    [Alimentation.SLDPRT, Arduino UNO.SLDASM, Body.SLDPRT, Body_2.SLDPRT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]
2018-06-28 Adding electrical designs. Again.
    [Alimentation.SLDPRT, Arduino UNO.SLDASM, Buton.SLDPRT, Chip.SLDASM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]
2018-06-28 Adding mechanical designs. Again.
    [Alimentation.SLDPRT, Arduino UNO.SLDASM, Body.SLDPRT, Body_2.SLDPRT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]
2018-06-28 Updated Fritzing diagram with battery
2018-07-16 Updated designs
    [Alimentation.SLDPRT, Arduino UNO.SLDASM, Body.SLDPRT, Body_2.SLDPRT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]
2018-07-16 Removing old files
    [Body.SLDPRT, Fin.SLDPRT, Fin_Left.SLDPRT, Fish_Assembly.SLDASM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]
2018-07-17 Removed unecessary files
    [Alimentation.SLDPRT, Arduino UNO.SLDASM, Buton.SLDPRT, Chip.SLDASM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]
2018-07-17 Removing unecessary files
    [HS-311_servo_horn.SLDPRT]
2018-07-17 Removed file, not required
    [HS-311_servo_horn.stp]
2018-07-17 Moved servo horn file
    [Servo_Horn.SLDPRT]
2018-08-22 Adding command flowchart here
2018-08-22 Updated with command flowchart
